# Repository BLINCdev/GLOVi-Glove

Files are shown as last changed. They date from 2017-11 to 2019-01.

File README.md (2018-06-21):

# GLOVi Glove
The Gesture Layout Observation Via Impedance (GLOVi) Glove was designed as an open-source data capture glove specifically designed for intuitive control of the HANDi Hand and may be also useful in other applications where quantification of finger flexion/extension movements is necessary. The inexpensive design allows low capital investment for pilot research studies or hobby projects, making it possible to provide proof-of-concept before investing in more robust or capable data capture gloves.

## Build your own GLOVi Glove
The GLOVi Glove consists of off-the-shelf potentiometers, electronic hardware, easy-to find materials, and custom 3D printed parts. Instructions for building the glove and setting up the potentiometers will be available in the near future, and will be your main go-to document while printing and building the glove.

* __3D Print Files:__ The folder that contains the raw STL files as well as the .THING and .x3g files for 3D printing on a Makerbot Replicator 2. NOTE: The STL files have been adjusted to print with proper tolerances in the PLA material. Further, the print orientation is important for many of the files; refer to the .thing files provided if printing .STL files with other softwares besides MakerWare to ensure the proper print orientation.
* __STEP Files:__ This folder contains the STEP files for each of the parts used in the hand, which should be importable into most 3D CAD softwares.
* __Arduino Sketches:__ This folder contains Arduino sketches that are used for controlling the HANDi hand. They can also be used as a basis for your own sketches should you be using the GLOVi Glove for some other purpose.

* __Bill of Materials:__ a detailed list of the off-the-shelf materials and parts required to build the GLOVi Glove. Note: We have listed the distributors that we have used in the past as a point of reference, but be aware that there are multiple distributor options for each part and that we do not endorse the listed distributors in any way.

If you would like to contribute to future official releases of the GLOVi Glove hardware we recommend contacting us on the [forums](https://blincdev.ca/forum/) to coordinate with our development team. To get started you will need to [fork this repo](https://help.github.com/articles/using-pull-requests/) and once your modification or enhancement is complete submit a [pull request](https://help.github.com/articles/using-pull-requests/).

## License
The GLOVi Glove hardware is released under the [Creative Commons BY-SA 4.0](http://creativecommons.org/licenses/by-sa/4.0/) license. A local copy of the license that was forked from [https://github.com/idleberg/Creative-Commons-4.0-Markdown](https://github.com/idleberg/Creative-Commons-4.0-Markdown) is available in the repository.

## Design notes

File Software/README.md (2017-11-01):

* __RN_rec:_ Arduino code for receiving Arduino Mega. Takes in bluetooth signals and writes positions to servos of HANDi Hand. Collects sensor data from HANDi Hand, and publishes it to GUI using Guino Library. Calibrated for right-handed HANDi Hand.

* __RN_rec_LH:_ Arduino code for receiving Arduino Mega. Takes in bluetooth signals and writes positions to servos of HANDi Hand. Collects sensor data from HANDi Hand, and publishes it to GUI using Guino Library. Calibrated for left-handed HANDi Hand.

* __RN_send:_ Arduino code for sending Arduino Leonardo via bluetooth. Takes in signals from GLOVi Glove and sends over bluetooth. Compatible with right or left-handed HANDi Hand.

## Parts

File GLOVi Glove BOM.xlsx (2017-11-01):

Item | Model Version | Part No. | Vendor | Quantity | Description | Notes
Breadboard | Wired / Bluetooth | 1597-1268-ND (digikey) 319030008 (mfg) | Digikey (https://www.digikey.ca/product-detail/en/seeed-technology-co-ltd/319030008/1597-1268-ND/5488152) | 1 | 4.5 X 3.5 cm mini breadboard
Capacitors | Wired / Bluetooth | 399-4299-ND (digikey) C320C334M5U5TA (mfg) | Digikey (https://www.digikey.ca/products/en?keywords=399-4299-nd) | 12 | 0.33 uF thru hole ceramic capacitors
Header Pins (40 pos) | Wired / Bluetooth | S1011EC-40-ND (digikey) PRPC040SAAN-RC (mfg) | Digikey (https://www.digikey.ca/products/en?keywords=s1011ec-40-nd) | 1 | Breakaway connectors, 2.54mm pitch
Potentiometers | Wired / Bluetooth | 490-2400-ND (digikey) SV01A103AEA01B00 (mfg) | Digikey (https://www.digikey.ca/product-detail/en/murata-electronics-north-america/SV01A103AEA01B00/490-2400-ND/588421) | 6 | Rotary Potentiometers
Resistors | Wired / Bluetooth | CF14JT10K0CT-ND (digikey) CF14JT10K0 (mfg) | Digikey (https://www.digikey.ca/products/en?keywords=CF14JT10K0CT-ND) | 12 | 10K thru hole resistors
Glove | Wired / Bluetooth | N/A | Dollar Store | 1 | Inexpensive stretch type glove
Dowel Pins | Wired / Bluetooth | 91585A261 | McMaster (https://www.mcmaster.com/) | 1 | 2mm diameter stainless steel dowel pins, 24mm long
String | Wired / Bluetooth | 87695K31 | McMaster (https://www.mcmaster.com/) | 1 | Nylon thread | Any small diameter nylon thread with relatively high tensile strength will do (i.e. good quality sewing thread for denim)
Torsion Springs (pack of 6) | Wired / Bluetooth | 9271K362 | McMaster (https://www.mcmaster.com/) | 1 | 270 degree left-hand torsion spring, 0.259" OD
Velcro Strapping | Wired / Bluetooth | 94905K629 | McMaster (https://www.mcmaster.com/) | 1 | Hook on one side, loop on the other 1/2 inch wide velcro strap
Wires | Wired / Bluetooth | 7071K19 | McMaster (https://www.mcmaster.com/) | 25 | Continuous Flex multi-strand 26 AWG wire
Scrap Cloth or Foam | Wired / Bluetooth | N/A | Scavenged | 1 | Any soft scrap cloth or thin foam (~1/4")
9V Battery | Bluetooth | P687-ND (digikey) 6LF22XWA/B (mfg) | Digikey (https://www.digikey.ca/product-detail/en/panasonic-bsg/6LF22XWA-B/P687-ND/5067196) | 1 | 9V battery
9V Battery to Barrel Jack Connector | Bluetooth | 1738-1339-ND (digikey) FIT0043 (mfg) | Digikey (https://www.digikey.ca/product-detail/en/dfrobot/FIT0043/1738-1339-ND/7597082) | 1 | 9V Battery to Barrel Jack Connector
Arduino Leonardo | Bluetooth | 1050-1040-ND (digikey) A000057 (mfg) | Digikey (https://www.digikey.ca/product-detail/en/arduino/A000057/1050-1040-ND/3476353) | 1 | Arduino Leonardo | Alternatively, Arduino Uno also fits in this design with no modification
Bluetooth Send/Receive | Bluetooth | 1568-1264-ND (digikey) WRL-12580 (mfg) | Digikey (https://www.digikey.ca/products/en?keywords=WRL-12580) | 2 | Bluetooth communication chip
LED Green | Bluetooth | 160-1710-ND (digikey) LTL-1CHG (mfg) | Digikey (https://www.digikey.ca/products/en?keywords=160-1710-nd) | 1 | Green LED
LED Red | Bluetooth | 160-1945-ND (digikey) LTL-1CHP | Digikey (https://www.digikey.ca/products/en?keywords=160-1945-ND) | 1 | Red LED
LED Yellow | Bluetooth | 160-1940-ND (digikey) LTL-1CHA (mfg) | Digikey (https://www.digikey.ca/products/en?keywords=160-1940-nd) | 1 | Yellow LED
Prototyping Wire | Bluetooth | 1568-1569-ND (digikey) PRT-08022 (mfg) | Digikey (https://www.digikey.ca/product-detail/en/sparkfun-electronics/PRT-08022/1568-1569-ND/6833928) | 1 | 22 AWG solid core prototyping wire
Nuts (pack of 100) | Bluetooth | 90591A121 | McMaster (https://www.mcmaster.com/) | 1 | M3 2.4mm thick hex nuts, pack of 100 | 4 needed for assembly
Screws (pack of 100) | Bluetooth | 91420A127 | McMaster (https://www.mcmaster.com/) | 1 | M3 18mm Philips head screws, pack of 100 | 4 needed for assembly

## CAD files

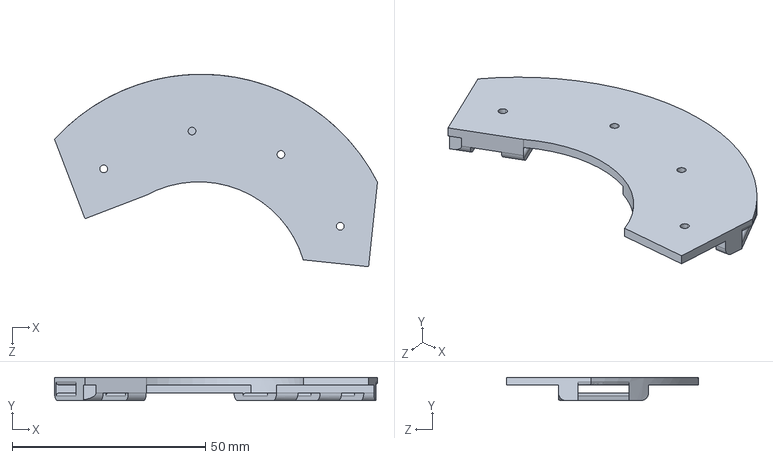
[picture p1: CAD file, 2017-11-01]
Hardware/.STEP Files/Back Plate.STEP
83.6 x 6.00 x 49.8 mm

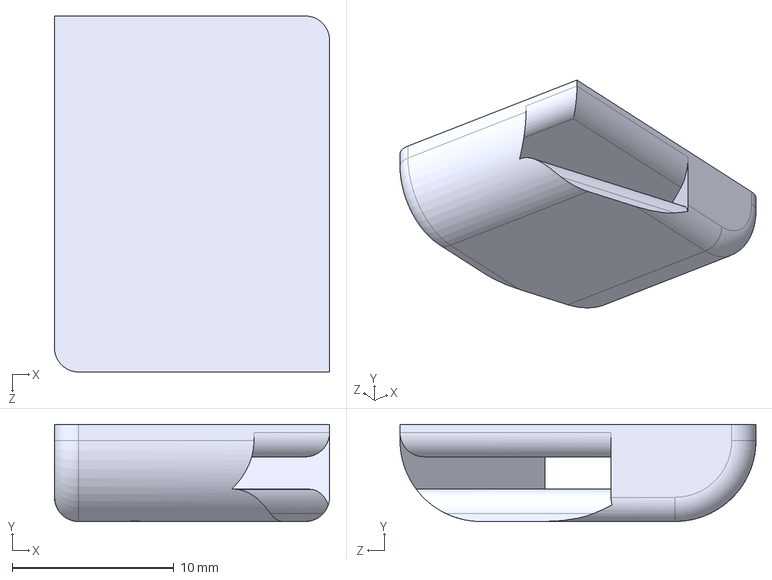
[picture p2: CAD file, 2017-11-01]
Hardware/.STEP Files/Thumb Rotator Backing.STEP
17.0 x 6.00 x 22.0 mm

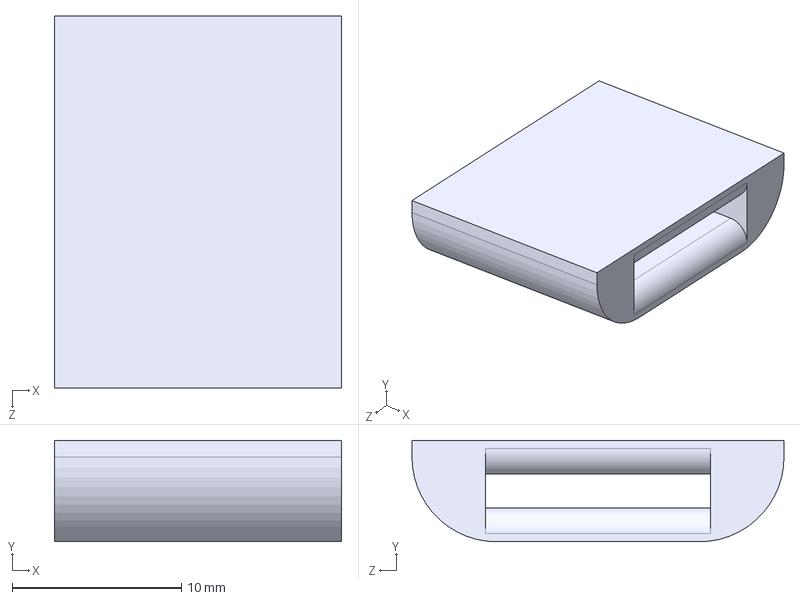
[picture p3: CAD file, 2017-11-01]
Hardware/.STEP Files/Thumb Flexor Backing.STEP
17.0 x 6.00 x 22.0 mm

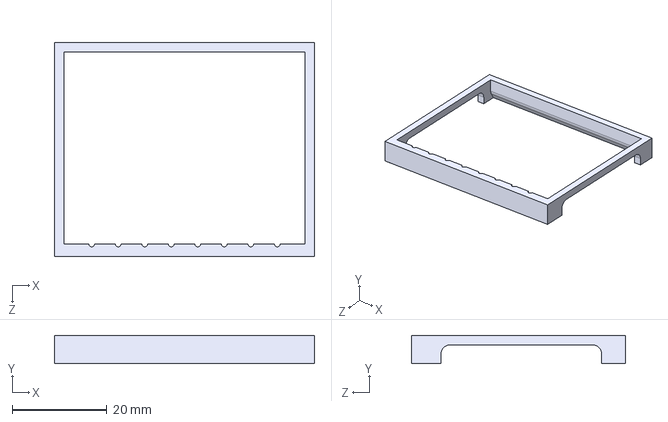
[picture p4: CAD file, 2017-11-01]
Hardware/.STEP Files/BGI Shroud.STEP
55.0 x 6.00 x 45.2 mm

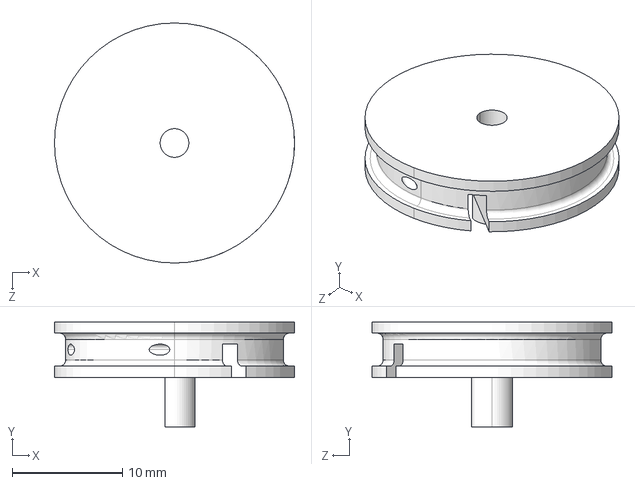
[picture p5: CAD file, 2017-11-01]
Hardware/.STEP Files/Spool.STEP
21.7 x 9.50 x 21.7 mm

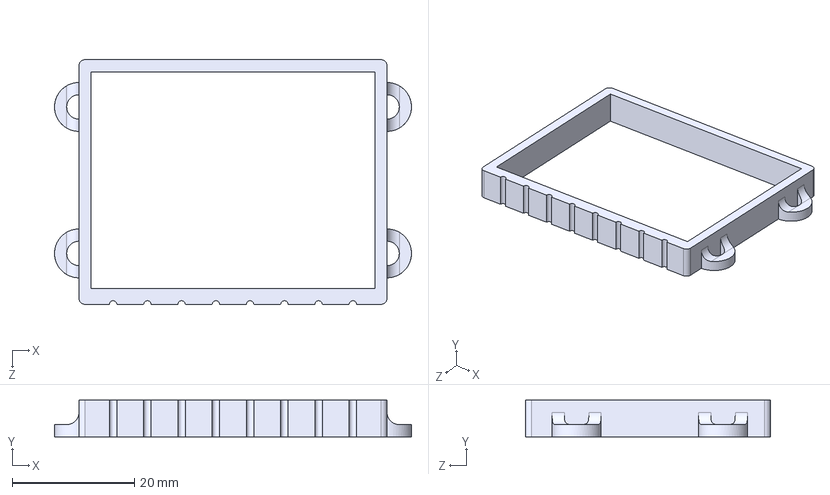
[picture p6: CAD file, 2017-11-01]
Hardware/.STEP Files/Breadboard to Glove Interface.STEP
58.5 x 6.00 x 40.1 mm

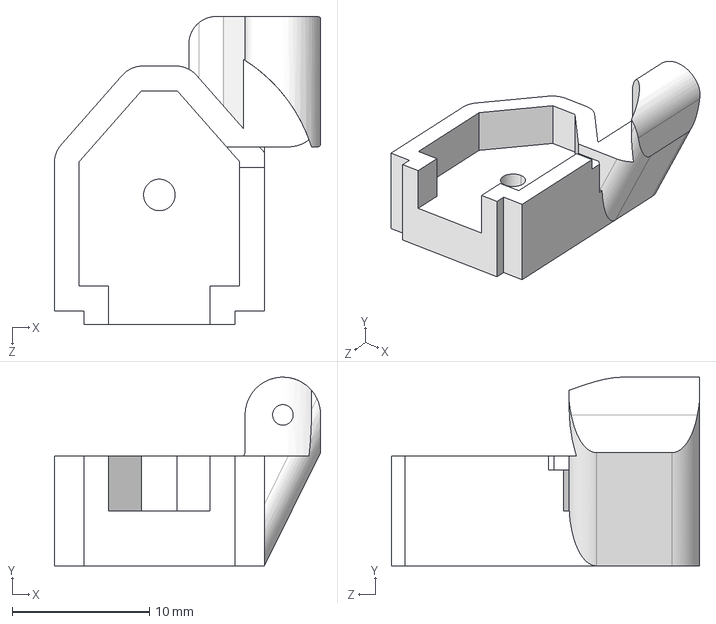
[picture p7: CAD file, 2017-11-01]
Hardware/.STEP Files/Pot Holder.STEP
19.4 x 13.7 x 22.4 mm

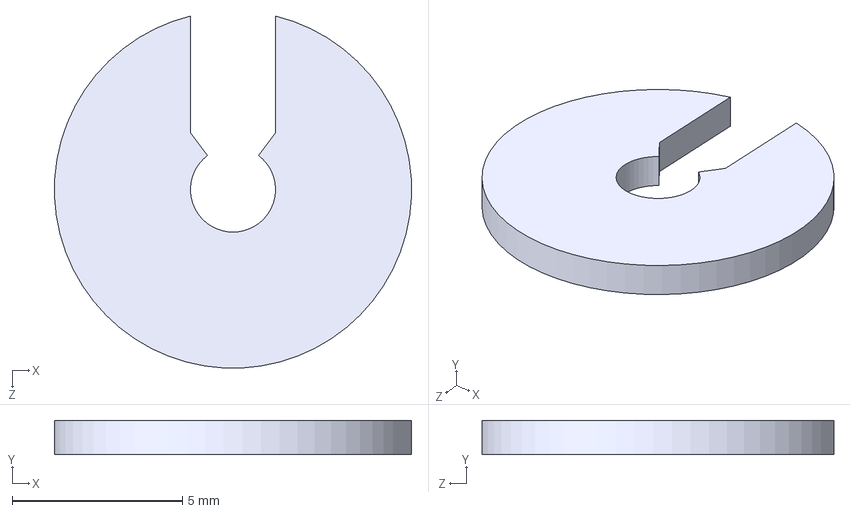
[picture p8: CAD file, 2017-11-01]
Hardware/.STEP Files/Spacer.STEP
10.5 x 1.00 x 10.3 mm

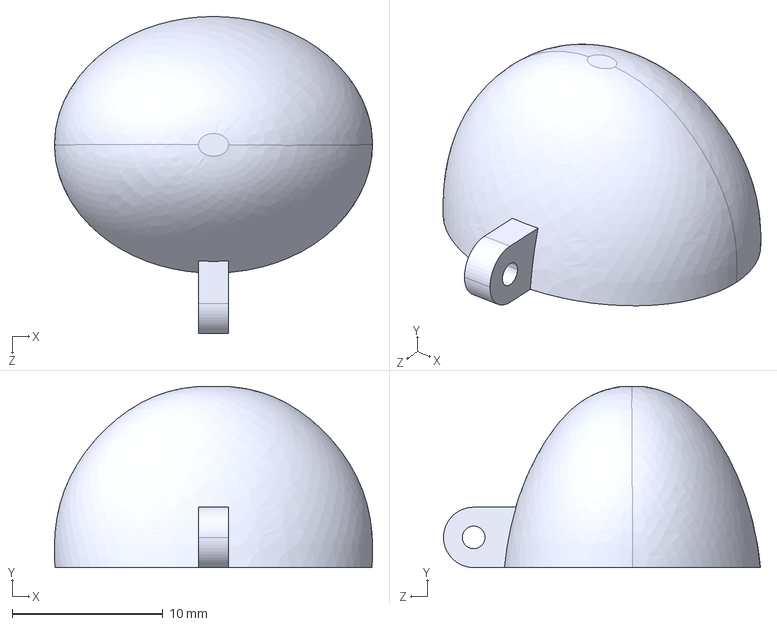
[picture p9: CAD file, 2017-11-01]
Hardware/.STEP Files/Formed Fingertip.STEP
21.1 x 12.0 x 21.0 mm

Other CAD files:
Hardware/.STL Files/BGI Shroud.STL
Hardware/.STL Files/Back Plate.STL
Hardware/.STL Files/Breadboard to Glove Interface.STL
Hardware/.STL Files/Cap.STL
Hardware/.STL Files/Formed Fingertip.STL
Hardware/.STL Files/Pot Holder.STL
Hardware/.STL Files/Spacer.STL
Hardware/.STL Files/Spool.STL
Hardware/.STL Files/Thumb Flexor Backing.STL
Hardware/.STL Files/Thumb Rotator Backing.STL

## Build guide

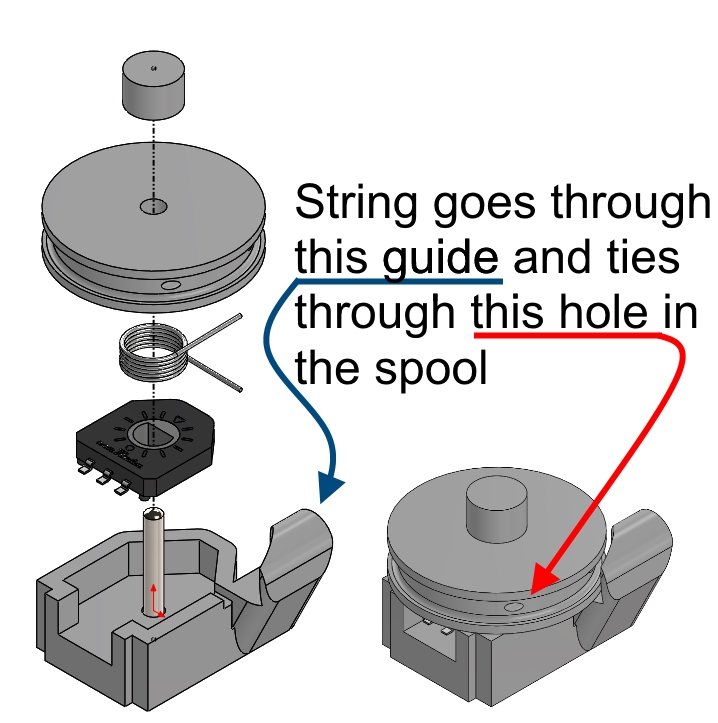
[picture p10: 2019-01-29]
Potentiometer Assembly Diagram.jpg

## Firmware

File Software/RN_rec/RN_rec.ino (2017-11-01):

#include <Boards.h>
#include <Firmata.h>

//This script incorporates bluetooth connection to Handi Hand via data glove with
//LED indicators for filter stabilization and GUI output of sensors to computer.
//25/05/2017 Dylan Brenneis, McNiel Keri

//#include <SoftwareSerial.h>
#include <Servo.h>

//servos
Servo D0_servo;  // create servo objects to control servos
Servo D1_servo;
Servo D2_servo;
Servo D3_servo;
Servo D4_servo;
Servo D5_servo;

//LEDs
int yel_led_1 = 40;  //Initialize LEDs for feedback of filter stabilization
int yel_led_2 = 42;
int yel_led_3 = 44;
int yel_led_4 = 46;
int grn_led = 48;

//Sensor Values
int D0_Angle = 0;
int D1P_Angle = 0;
int D1D_Angle = 0;
int D2P_Angle = 0;
int D2I_Angle = 0;
int D3P_Angle = 0;
int D3I_Angle = 0;
int D4P_Angle = 0;
int D5P_Angle = 0;
  
int D4I_Angle = -10; //dummy variable for spacing in GUI
int D5I_Angle = -10; //dummy variable for spacing in GUI
  
int D1_Voltage = 0;
int D2_Voltage = 0;
int D3_Voltage = 0;
int D4_Voltage = 0;
int D5_Voltage = 0;

//Potentiometer Max and Min readouts for mapping to degrees of flexion:
int D0_max = 175;
int D0_min = 0;
int D1P_max = 301;
int D1P_min = 487;
int D1D_max = 336;
int D1D_min = 515;
int D2P_max = 289;
int D2P_min = 512;
int D2I_max = 264;
int D2I_min = 518;
int D3P_max = 759;
int D3P_min = 530;
int D3I_max = 270;
int D3I_min = 500;
int D4P_max = 753;
int D4P_min = 500;
int D5P_max = 755;
int D5P_min = 568;
  
//setup bluetooth serial connection
int const BLUETOOTH_SETTLE_TIME = 100;

// Recieve buffer
byte const FLAG = 0x2E; //"Ascii period": Flag used to identify start of stream
byte recieveBuffer[12];               // Receive buffer

////variables
int D0_pos = -1;
int D1_pos = -1;
int D2_pos = -1;
int D3_pos = -1;
int D4_pos = -1;
int D5_pos = -1;

int D0_servo_pos = 0;
int D1_servo_pos = 0;
int D2_servo_pos = 0;
int D3_servo_pos = 0;
int D4_servo_pos = 0;
int D5_servo_pos = 0;

int currentAndPastInput[7][6] = {{0, 0, 0, 0, 0, 0}, {0, 0, 0, 0, 0, 0}, {0, 0, 0, 0, 0, 0}, {0, 0, 0, 0, 0, 0}, {0, 0, 0, 0, 0, 0}, {0, 0, 0, 0, 0, 0}, {0, 0, 0, 0, 0, 0}}; //4th order - 6th order : length 4-6
//currentAndPastInput = [D0_pos,D1_pos,D2_pos,D3_pos,D4_pos,D5_pos] => {{current},{n-1} -> {n-6}}
float currentAndPastOutput[7][6] = {{0.0, 0.0, 0.0, 0.0, 0.0, 0.0}, {0.0, 0.0, 0.0, 0.0, 0.0, 0.0}, {0.0, 0.0, 0.0, 0.0, 0.0, 0.0}, {0.0, 0.0, 0.0, 0.0, 0.0, 0.0}, {0.0, 0.0, 0.0, 0.0, 0.0, 0.0}, {0.0, 0.0, 0.0, 0.0, 0.0, 0.0}, {0.0, 0.0, 0.0, 0.0, 0.0, 0.0}}; //4th order - 6th order : length 4-6
//currentAndPastOutput = [D0_pos,D1_pos,D2_pos,D3_pos,D4_pos,D5_pos] => {{current},(n-1) -> {n-6}}
//samples to reach steady state for step impluse => matlab
int const SAMPLES_FOR_SS_2thOrder = BLUETOOTH_SETTLE_TIME + 100; // 92 exactly

int programCounter = 0;
int numberOfSamplesRecieved = 0;

void setup()
{
  //Set up serial And BT
  Serial.begin(38400);  // Begin the serial monitor at 38400bps
  Serial1.begin(38400);  // Begin Bluetooth
  gBegin(38400);// Set up GUI for output

  // set servo objects to appropriate pins
  D0_servo.attach(3);
  D1_servo.attach(5);
  D2_servo.attach(6);
  D3_servo.attach(9);
  D4_servo.attach(10);
  D5_servo.attach(11);
  
  //Initialize LEDs
  pinMode(yel_led_1, OUTPUT);
  pinMode(yel_led_2, OUTPUT);
  pinMode(yel_led_3, OUTPUT);
  pinMode(yel_led_4, OUTPUT);
  pinMode(grn_led, OUTPUT);

}

void loop()
{
  //**** Main update call for the guino:
  guino_update();
  
  // Bluetooth receive
  if (Serial1.available() >= sizeof(recieveBuffer)) // If there's anything to read
  {
    if ( Serial1.read() * 256 + Serial1.read() == FLAG) {

      if (Serial1.read() * 256 + Serial1.read() == FLAG) {

        Serial1.readBytes(recieveBuffer, sizeof(recieveBuffer));
        numberOfSamplesRecieved =  numberOfSamplesRecieved + 1;
        //variables
        D0_pos = (int)(recieveBuffer[0] * 256 + recieveBuffer[1]);
        D1_pos = (int)(recieveBuffer[2] * 256 + recieveBuffer[3]);
        D2_pos = (int)(recieveBuffer[4] * 256 + recieveBuffer[5]);
        D3_pos = (int)(recieveBuffer[6] * 256 + recieveBuffer[7]);
        D4_pos = (int)(recieveBuffer[8] * 256 + recieveBuffer[9]);
        D5_pos = (int)(recieveBuffer[10] * 256 + recieveBuffer[11]);

        D0_pos = map(D0_pos , 450, 700, 180, 0); //scale it to use it with the servo (value between 0 and 180)
        D1_pos = map(D1_pos , 350, 700, 180, 0);
        D2_pos = map(D2_pos , 450, 900, 180, 0);
        D3_pos = map(D3_pos , 350, 750, 180, 0);
        D4_pos = map(D4_pos , 400, 800, 180, 0);
        D5_pos = map(D5_pos , 400, 800, 180, 0);

        D0_pos = min(max(D0_pos, 0), 180); //scale it to use it with the servo (value between 0 and 180)
        D1_pos = min(max(D1_pos, 0), 180);
        D2_pos = min(max(D2_pos, 0), 180);
        D3_pos = min(max(D3_pos, 0), 180);
        D4_pos = min(max(D4_pos, 0), 180);
        D5_pos = min(max(D5_pos, 0), 180);


        // shift old output to n-1 position so filters do not overwrite it with the new output position
        //update inputs array load new input to current position and push everything else down by one.
        shiftInputAndOutPutArrays();

        if (numberOfSamplesRecieved > BLUETOOTH_SETTLE_TIME) { //inital bluetooth transmission is not always stable, wait for a few samples before engaging filter
          //filter current output 2th order
          secondOrderButterLPF_cutoff_20Hz_difference_equation();



          if (numberOfSamplesRecieved > SAMPLES_FOR_SS_2thOrder) //filter reached steady state
          {
//            Serial.println(min(max(currentAndPastOutput[0][2], 0), 180));;

            //recall
            //currentAndPastOutput = [D0_pos,D1_pos,D2_pos,D3_pos,D4_pos,D5_pos] => {{current},(n-1) -> {n-6}}
             D0_servo_pos = (min(max(currentAndPastOutput[0][0], 0), 180)); //sets the servo position according to the scaled value
             D1_servo_pos = (min(max(currentAndPastOutput[0][1], 0), 180));
             D2_servo_pos = (min(max(currentAndPastOutput[0][2], 0), 180));
             D3_servo_pos = (min(max(currentAndPastOutput[0][3], 0), 180));
             D4_servo_pos = (min(max(currentAndPastOutput[0][4], 0), 180));
             D5_servo_pos = (min(max(currentAndPastOutput[0][5], 0), 180));
             
             D0_servo.write(D0_servo_pos); //sets the servo position according to the scaled value
             D1_servo.write(D1_servo_pos);
             D2_servo.write(D2_servo_pos);
             D3_servo.write(D3_servo_pos);
             D4_servo.write(D4_servo_pos);
             D5_servo.write(D5_servo_pos);
                         
             digitalWrite(yel_led_1,LOW);
             digitalWrite(yel_led_2,LOW);
             digitalWrite(yel_led_3,LOW);
             digitalWrite(yel_led_4,LOW);
             digitalWrite(grn_led,HIGH);
          } 
        else
        {
          Serial.println(numberOfSamplesRecieved);
          if (numberOfSamplesRecieved <= BLUETOOTH_SETTLE_TIME + 33)
          {
          digitalWrite(yel_led_1,LOW);
          digitalWrite(yel_led_2,HIGH);
          digitalWrite(yel_led_3,LOW);
          digitalWrite(yel_led_4,LOW);
          digitalWrite(grn_led,LOW);
          }
          else
          {
          if (numberOfSamplesRecieved < BLUETOOTH_SETTLE_TIME + 66)
          {
          digitalWrite(yel_led_1,LOW);
          digitalWrite(yel_led_2,LOW);
          digitalWrite(yel_led_3,HIGH);
          digitalWrite(yel_led_4,LOW);
          digitalWrite(grn_led,LOW);
          }
          else{          
          digitalWrite(yel_led_1,LOW);
          digitalWrite(yel_led_2,LOW);
          digitalWrite(yel_led_3,LOW);
          digitalWrite(yel_led_4,HIGH);
          digitalWrite(grn_led,LOW);          
          }
          }
        }
        }
        else
        {
          digitalWrite(yel_led_1,HIGH);
          digitalWrite(yel_led_2,LOW);
          digitalWrite(yel_led_3,LOW);
          digitalWrite(yel_led_4,LOW);
          digitalWrite(grn_led,LOW);           
        }
      }

    }

  }
  programCounter = programCounter + 1;
  
  // Read in the values from each of the potentiometers and FSRs:
  int D0_Voltage = analogRead(A2);
  int D1P_Voltage = analogRead(A3);
  int D1D_Voltage = analogRead(A4);
  int D2P_Voltage = analogRead(A5);
  int D2I_Voltage = analogRead(A6);
  int D3P_Voltage = analogRead(A7);
  int D3I_Voltage = analogRead(A8);
  int D4P_Voltage = analogRead(A9);
  int D5P_Voltage = analogRead(A10);
  D1_Voltage = analogRead(A11);
  D2_Voltage = analogRead(A12);
  D3_Voltage = analogRead(A13);
  D4_Voltage = analogRead(A14);
  D5_Voltage = analogRead(A15);
  
    // Map the Potentiometer voltages to % flexion:
  D0_Angle = map(D0_Voltage,D0_min,D0_max,100,0);
  D1P_Angle = map(D1P_Voltage,D1P_min,D1P_max,100,0);
  D1D_Angle = map(D1D_Voltage,D1D_min,D1D_max,100,0);
  D2P_Angle = map(D2P_Voltage,D2P_min,D2P_max,100,0);
  D2I_Angle = map(D2I_Voltage,D2I_min,D2I_max,100,0);
  D3P_Angle = map(D3P_Voltage,D3P_min,D3P_max,100,0);
  D3I_Angle = map(D3I_Voltage,D3I_min,D3I_max,100,0);
  D4P_Angle = map(D4P_Voltage,D4P_min,D4P_max,100,0);
  D5P_Angle = map(D5P_Voltage,D5P_min,D5P_max,100,0);
  
  // Send the values to the GUI:
  gUpdateValue(&D0_Angle);
  gUpdateValue(&D1P_Angle);
  gUpdateValue(&D1D_Angle);
  gUpdateValue(&D2P_Angle);
  gUpdateValue(&D2I_Angle);
  gUpdateValue(&D3P_Angle);
  gUpdateValue(&D3I_Angle);
  gUpdateValue(&D4P_Angle);
  gUpdateValue(&D5P_Angle);
  gUpdateValue(&D1_Voltage);
  gUpdateValue(&D2_Voltage);
  gUpdateValue(&D3_Voltage);
  gUpdateValue(&D4_Voltage);
  gUpdateValue(&D5_Voltage);
  
}

void shiftInputAndOutPutArrays()
{
  //shift both arrays downward by one row
  for (int i = 6; i >= 0 ; i--) // process all seven rows
  { 
    for (int j = 0; j <= 5; j++) { //for all the columns
      if (i > 0) // for everything by the first row
      { //recall [D0_pos,D1_pos,D2_pos,D3_pos,D4_pos,D5_pos]
        currentAndPastOutput[i][j] = currentAndPastOutput[i - 1][j]; //assign the current row the values of the previous row
        currentAndPastInput[i][j] = currentAndPastInput[i - 1][j];
      }
      else
      {
        //set current output as zeros (will be replaced will filtered afterwards)
        currentAndPastOutput[0][0] = 0;
        currentAndPastOutput[0][1] = 0;
        currentAndPastOutput[0][2] = 0;
        currentAndPastOutput[0][3] = 0;
        currentAndPastOutput[0][4] = 0;
        currentAndPastOutput[0][5] = 0;
        //set current inputs as the mapped inputs
        currentAndPastInput[0][0] = D0_pos;
        currentAndPastInput[0][1] = D1_pos;
        currentAndPastInput[0][2] = D2_pos;
        currentAndPastInput[0][3] = D3_pos;
        currentAndPastInput[0][4] = D4_pos;
        currentAndPastInput[0][5] = D5_pos;
      }
    }
  }
}

void firstOrderButterLPF_cutoff_20Hz_difference_equation()
{ //needs length(currentAndPastInput) = 5, length(pAstOutPut) = 5
  //cutoff 160
  const float A[] = {1,-0.725343};
  const float B[] = {0.137328,0.137328};

  float K =1.25;
  for (int i = 0; i <= 5 ; i++) { //6 - columns
    //updating current outputs
    currentAndPastOutput[0][i] = (-A[1] * (float)currentAndPastOutput[1][i]+ K*(B[0] * (float)currentAndPastInput[0][i] + B[1] * (float)currentAndPastInput[1][i]));
  }
}
void secondOrderButterLPF_cutoff_20Hz_difference_equation()
{ 
  //160 Hz
  const float A[] = {1,-1.558868,0.639930};
  const float B[] = {0.020265,0.040531,0.020265};
  float K = 1.25;
  
  for (int i = 0; i <= 5 ; i++) { //6 - colums
    currentAndPastOutput[0][i] = (-A[1] * (float)currentAndPastOutput[1][i] - A[2] * (float)currentAndPastOutput[2][i] + K*( B[0] * (float)currentAndPastInput[0][i] + B[1] * (float)currentAndPastInput[1][i] + B[2] * (float)currentAndPastInput[2][i]));  
  }

}
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

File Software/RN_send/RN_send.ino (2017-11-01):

#include <SoftwareSerial.h>  

//grab six analog signals of the hand from data glove, (thumb flexion/extension [F/E] & Add/Adbuction [Ad/Ab])
//pins layout
const int D0 = A0; // Thumb Ad/Ab 
const int D1 = A1; // Thumb F/E
const int D2 = A2; // Index
const int D3 = A3; // Middle
const int D4 = A4; // Ring finger 
const int D5 = A5; // Pinky
//variables 
int D0_pos = 0;           
int D1_pos = 0;
int D2_pos = 0;
int D3_pos = 0;
int D4_pos = 0;
int D5_pos = 0;



//setup blue tooth serial connection
const int BLUETOOTH_TX = 2;  // TX-O pin of RN-42, Arduino D2
const int BLUETOOTH_RX = 4;  // RX-I pin of RN-42, Arduino D4
SoftwareSerial bluetooth(BLUETOOTH_TX, BLUETOOTH_RX);

// Send buffer
byte const FLAG = 0x2E; //"ascii period": Flag used to identify start of stream
byte sendBuffer[16];                 // Sendbuffer

void setup()
{
  Serial.begin(38400);  // Begin the serial monitor at 9600bps

  bluetooth.begin(38400);  // The Bluetooth Mate defaults to 115200bps
}

void loop()
{
  //grab current hand positions
  D0_pos = analogRead(D0);           
  D1_pos = analogRead(D1);
  D2_pos = analogRead(D2);
  D3_pos = analogRead(D3);
  D4_pos = analogRead(D4);
  D5_pos = analogRead(D5);

  sendInfo();
  delay(50);
//   Serial.println("^^^^^^^^^^^^^^^^^^^^^^^^");
        Serial.print(String(D0_pos));
        Serial.print(", ");
        Serial.print(String(D1_pos));
        Serial.print(", ");
        Serial.print(String(D2_pos));
        Serial.print(", ");
        Serial.print(String(D3_pos));
        Serial.print(", ");
        Serial.print(String(D4_pos));
        Serial.print(", ");
        Serial.println(String(D5_pos));
}

// Send information to the computer via Bluetooth
void sendInfo()
{
  // Fill byte buffer with sensor data
  // The first two are flags to know when to start looking at the streaming data
  // Each sensor data stores the upper byte and lower byte, since the byte buffer only takes one byte at a time
  // This is more light weight than sending strings, int, double etc since the information from the sensor 
  // Will most likely not exceed 2^16 (two bytes) as the ADC maps values to 10bit -> 2^10.

  // Load flags, 4 periods "...."
  sendBuffer[0]= FLAG >> 8;
  sendBuffer[1]= FLAG & 0xFF;
  sendBuffer[2]= FLAG >> 8;
  sendBuffer[3]= FLAG & 0xFF;
//  sendBuffer[4]= FLAG >> 8;
//  sendBuffer[5]= FLAG & 0xFF;
//  sendBuffer[6]= FLAG >> 8;
//  sendBuffer[7]= FLAG & 0xFF;
  
  int i = 4; //8 buffer_offset
  // Load data glove values
  sendBuffer[i] = D0_pos >>8;     // thumbAx UB: UpperByte 
  sendBuffer[i+1] = D0_pos & 0xFF;  // thumbAx LB: LowerByte 
  sendBuffer[i+2] = D1_pos >> 8;    // thumbFE UB
  sendBuffer[i+3] = D1_pos & 0xFF;  // thumbFE LB
  sendBuffer[i+4] = D2_pos >> 8;    // indexF UB
  sendBuffer[i+5] = D2_pos & 0xFF;  // indexF LB
  sendBuffer[i+6]= D3_pos >> 8;    // middleF UB
  sendBuffer[i+7]= D3_pos & 0xFF;  // middleF LB
  sendBuffer[i+8]= D4_pos >> 8;    // ringF UB
  sendBuffer[i+9]= D4_pos & 0xFF;  // ringF LB
  sendBuffer[i+10]= D5_pos >> 8;    // pinkyF UB
  sendBuffer[i+11]= D5_pos & 0xFF;  // pinkyF LB
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

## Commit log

2017-11-01 Uploaded Hardware and Software files, BOM, and README
    [BGI Shroud.STEP, BGI Shroud.STL, Back Plate.STEP, Back Plate.STL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]
2019-01-29 Included Potentiometer Assembly Diagram
